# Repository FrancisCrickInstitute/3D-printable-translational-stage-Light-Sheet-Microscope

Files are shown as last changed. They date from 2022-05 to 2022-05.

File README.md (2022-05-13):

# 3D printable translational stage Light Sheet Microscope

In this technical note we present a fully 3D printable linear stage designed to give the researchers a tool to acquire equally spaced images 
using the LaVision Light sheet Microscope. The pitch of the M2 thread measures 0.4 mm therefore, rotational movements of half or even a quarted 
of revolution of the screw placed on the middle will be linear increments of 200 and 100 µm respectively. The range of movement of the platform 
is 36 mm.



Figure 1: Design of the stage on the CAD software.

Assembly instructions
This device has been printed using a Form 3 3D printer filled with clear V4 resin. It has been printed using the standard settings (100 µm resolution).
1-	Remove the support material of both pieces.
2-	Use a hand tap set M2 size to thread the holes for the screws.



Figure 2: M2 tap hand tool (left) and Threaded M2 holes (right).
 
Figure 2: M2 tap hand tool (left) and Threaded M2 holes (right).
3-	Insert the two M2 screws that act as a guides while you place the platform holes on the path of the screws.
4-	Now insert the embedded M2 nut and insert the center M2 screw threading inside the embedded nut.
5-	Insert the M2 self-locking nut on the other side of the central screw, this nut limits the axial displacement of the screw. The nut has to be threaded on the nylon side. Alternatively, a regular M2 nut can be used with thread locking glue inside the thread (RS Components 693-848).



Figure 3: Completed assembly.

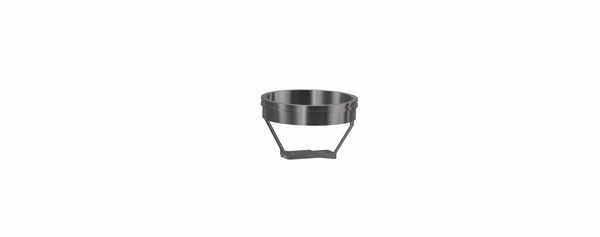
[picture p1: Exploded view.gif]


Figure 4: Exploded assembly

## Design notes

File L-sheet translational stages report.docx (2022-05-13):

3D printable translational stage for LaVision Light Sheet Microscope

In this technical note we present a fully 3D printable linear stage designed to give the researchers a tool to acquire equally spaced images using the LaVision Light sheet Microscope. The pitch of the M2 thread measures 0.4 mm therefore, rotational movements of half or even a quarted of revolution of the screw placed on the middle will be linear increments of 200 and 100 µm respectively. The range of movement of the platform is 36 mm.

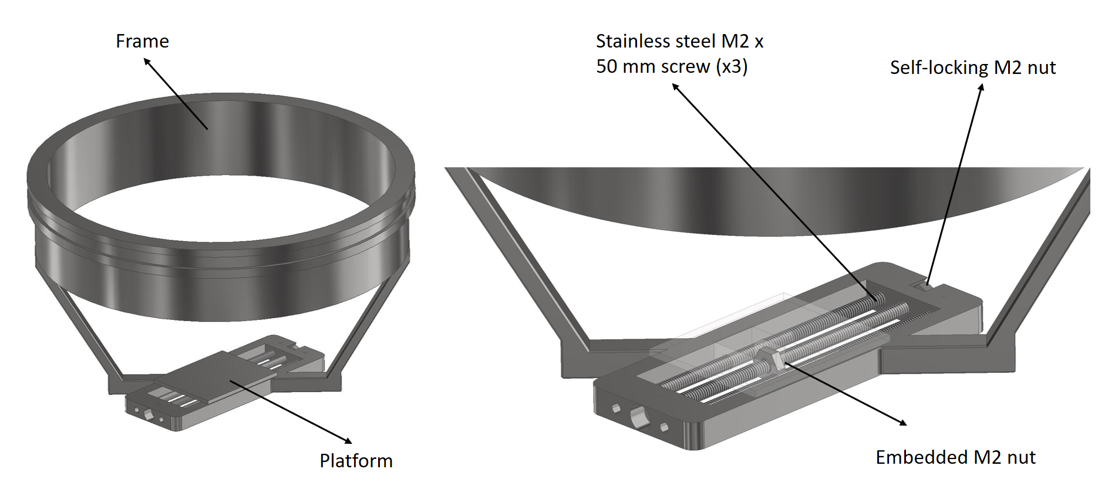
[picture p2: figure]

Figure 1: Design of the stage on the CAD software.

Bill of materials

Part | Quantity | Reference
Custom frame | 1 | STL/STEP file
Platform | 1 | STL/STEP file
M2 x 50 mm screws | 3 | https://www.amazon.co.uk/sourcingmap-Stainless-Steel-Phillips-Screws/dp/B012TDJE3O/ref=asc_df_B012TDJE3O/?tag=googshopuk-21&linkCode=df0&hvadid=272054178218&hvpos=&hvnetw=g&hvrand=16044810879815880919&hvpone=&hvptwo=&hvqmt=&hvdev=c&hvdvcmdl=&hvlocint=&hvlocphy=9045999&hvtargid=pla-319427555651&psc=1
M2 nut | 1 | https://uk.rs-online.com/web/p/hex-nuts/2484551/
M2 self-locking nut | 1 | https://www.amazon.co.uk/Stainless-Self-locking-Anti-loose-Locknut-M2-100Pcs/dp/B075V8KNWY/ref=sr_1_3_sspa?dchild=1&keywords=M2+self+locking+nut&qid=1601645287&sr=8-3-spons&psc=1&smid=A5QX2SUPA7LK7&spLa=ZW5jcnlwdGVkUXVhbGlmaWVyPUFNQ1BIWFFYMlIzV0UmZW5jcnlwdGVkSWQ9QTAyMDg1NDQzVjdXTTdXRlpXWkNOJmVuY3J5cHRlZEFkSWQ9QTA1NDg0MjEzVThRSzRXQkI1UjMyJndpZGdldE5hbWU9c3BfYXRmJmFjdGlvbj1jbGlja1JlZGlyZWN0JmRvTm90TG9nQ2xpY2s9dHJ1ZQ==

Assembly instructions

This device has been printed using a Form 3 3D printer filled with clear V4 resin. It has been printed using the standard settings (100 µm resolution).

1- Remove the support material of both pieces.
2- Use a hand tap set M2 size to thread the holes for the screws.

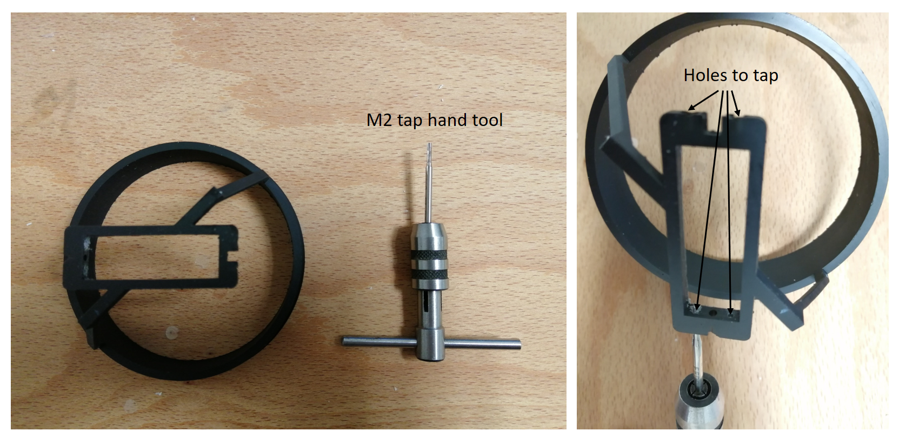
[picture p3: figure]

Figure 3: M2 tap hand tool (left) and Threaded M2 holes (right).

3- Insert the two M2 screws that act as a guides while you place the platform holes on the path of the screws.
4- Now insert the embedded M2 nut and insert the center M2 screw threading inside the embedded nut.
5- Insert the M2 self-locking nut on the other side of the central screw, this nut limits the axial displacement of the screw. The nut has to be threaded on the nylon side. Alternatively, a regular M2 nut can be used with thread locking glue inside the thread (RS Components 693-848).

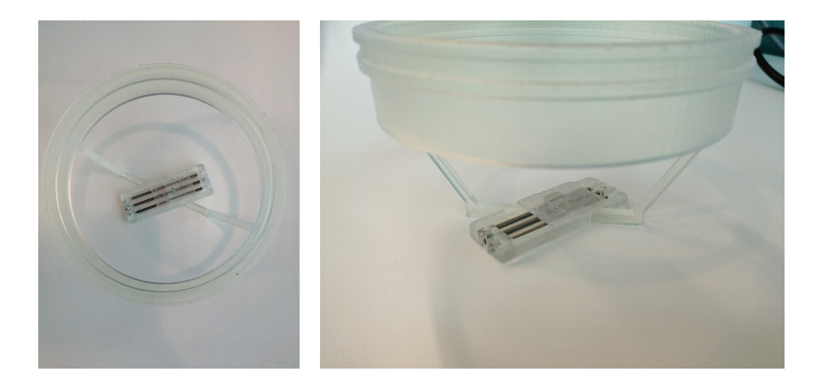
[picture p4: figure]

Figure 2: Completed assembly.

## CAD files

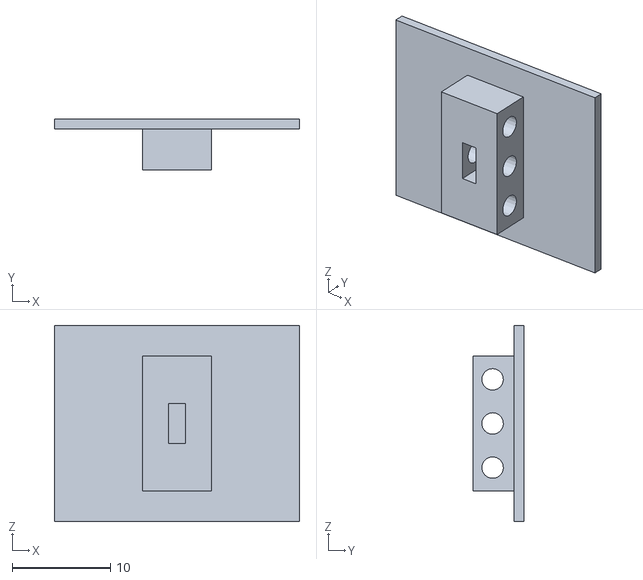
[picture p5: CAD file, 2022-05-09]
Manufacturing files/Moving platform for big samples.stl
25.0 x 5.20 x 20.0

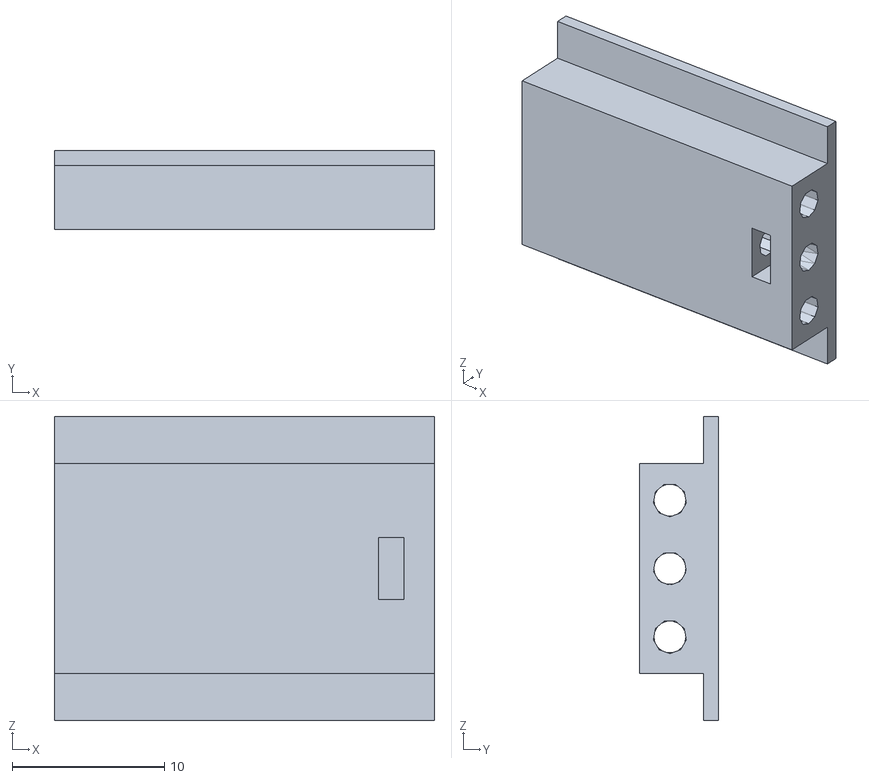
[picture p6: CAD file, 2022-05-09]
Manufacturing files/Moving platform.stl
25.0 x 5.20 x 20.0

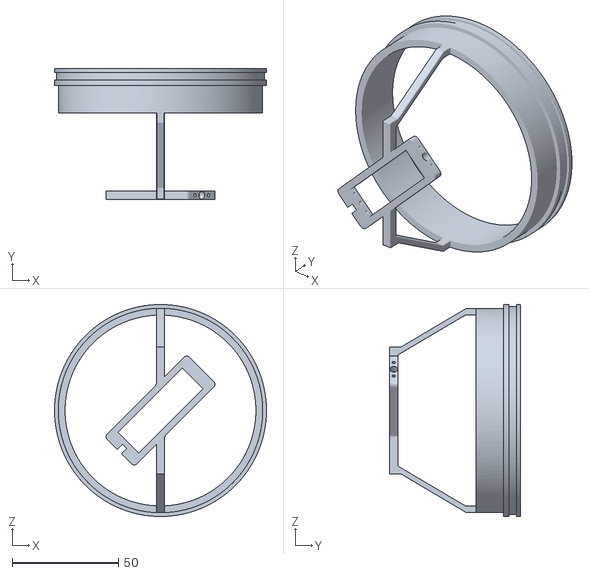
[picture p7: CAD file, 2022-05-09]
Manufacturing files/Custom_frame_1.stl
100.0 x 61.8 x 100.0

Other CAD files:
Design files/Custom frame assembly.iam
Design files/Custom_frame_1.ipt
Design files/Custom_frame_2(No translation).ipt
Design files/Frame.ipt
Design files/ISOM2 x 50 mm.ipt
Design files/M2 nut.ipt
Design files/Moving platform.ipt
Design files/Spring.ipt
